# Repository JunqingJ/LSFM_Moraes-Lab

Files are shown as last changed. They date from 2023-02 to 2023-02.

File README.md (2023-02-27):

# LSFM_Moraes-Lab
A customized Oblique Plane Microscope (OPM) based on the design of SCPAE 2.0 published by Prof. Hillman. The microscope is primarily customized to image non-cleared brain organoids during the early development stage for quality control purposes.

The repository is currently work in progress and will eventually contain all information (alignment procedure, part list, design files for machined items, controlling code) need to re-build the same setup.

It is also highly suggested for anyone new to light-sheet microscopy to consult Alfred Millett-Sikking's work(https://github.com/amsikking). The setup shown in this repository had received tremendous amount of help form Alfred and many design is also inspired by his work. 

Schematic diagram of the setup:

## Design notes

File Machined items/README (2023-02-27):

ARCOpticThreads.xml - Threading file for Fusion 360 to generate internal/external SM1 threading. 
To use it, add the .xml file into local threading data folder of Fusion360
Folder address ((C:\Users\%Username%\AppData\Local\Autodesk\webdeploy\production\%Version number%\Fusion\Server\Fusion\Configuration\ThreadData))

CCM_G01 side mount plate - Fusion 360 design file. CCM_G01 is design to turn the light in xy plane. In case the light to be turned into z axis, a side mounting is need

Sample stage arm - the stage arm is designed to fit onto Picard 4D stage to hold a 35mm petri dish with set screw

Slide git Powell mount - The mount is designed to adapt a 8.9mm Powell lens from Laserline Optics into 30mm cage palte from Thorlabs. 
It is important to ask for Slide fit when machining

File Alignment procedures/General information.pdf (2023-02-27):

General information

The overall setup of the microscope is shown in Figure 1 with laser been represented by blue and

fluorescent light been represented by green. The overall setup is further divided into 4 subsections

for details of alignment procedures and equipment used for assembling will be listed at the end of

each section. It should be noticed that all optics were setup on a secondary breadboard that was

elevated around 5inch higher than the optical table. The illumination laser was setup on a separate

breadboard that is elevated around 1.5inch higher than the first one. This is done so that it provides

enough space in z-direction for the alignment of optics and electronics could also been housed

under elevated breadboard to save space. In addition, a bright-field imaging system was added in

section 1 by using a removable turning mirror 2, S3, T4 and camera 2. This is done so that it

provides the system a much easier way to locate the sample and the region of interest prior to the

3D scanning.

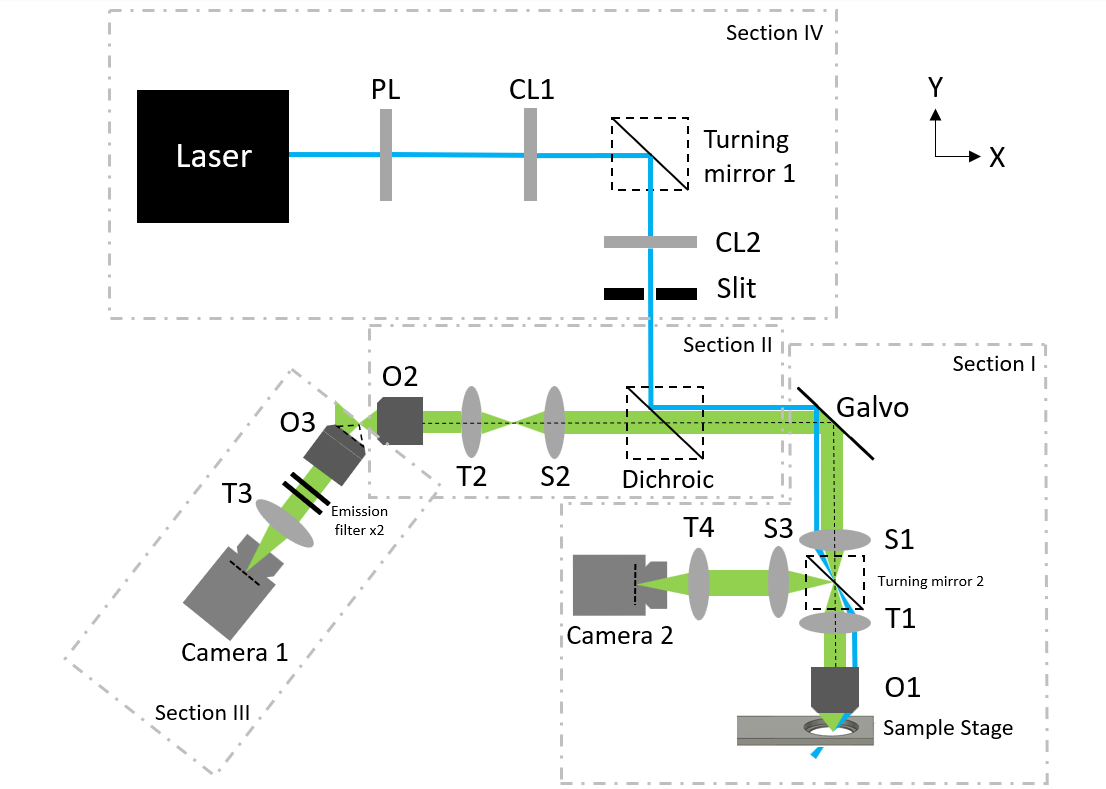
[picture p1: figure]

Figure 1 Overall setup of the microscope with subsections

Apart from the equipment and tools used in individual sections, several other equipment was used

throughout the entire process for the calibration and mounting purpose. Cage system is widely

used within the system to facilitate easier mounting and alignment. Both 30mm and 60mm cage

system are used due to the need of lens in different size. As a result, generic naming will be used

regarding cage system in subsections and the amount used will be detailed in tables. For calibration

purpose, a shear plate compatible with beam size from 1-3mm (Thorlabs, SI035) were used to test

collimation of beams. Another 4.5mW collimated laser module at 532nm with 3.5mm round beam

size (Thorlabs, CPS532) were used to assist the alignment. The collimated laser module was fitted

into the 30mm cage system by a SM1-threaded adaptor (Thorlabs, AD11F) and mounted onto a

quick-release cage plate (Thorlabs, CP44F). In addition, both post-mountable and cage system iris

diaphragms (Thorlabs, ID25 and CP20D) were used for lens positioning. Finally, laser viewing

cards (Thorlabs, VRC1 and VRC2) were used to visualize the laser beam while minimizing its

potential harm to eyes.

Before any part of the microscope was assembled, a 30×48inch optical table with 4inch thick

breadboard (Newport, VIS3048-PG4-325A) was inflated using compressed nitrogen. The flatness

of the surface was first checked by making sure the bubble leveler on each stand of the optical

table was centered. After that, illumination laser (HUBNER Photonics) was used, and the height

of the laser beam was measured over a long distance for verification. It is important to use the

minimal laser power available (~1mW) during the flatness verification and a laser safety glass (ex.

Thorlabs, LG14) should be used based on the wavelength of the laser used.

Table 1 General items used throughout all alignment processes

Item description | Part number (Vendor)
Shear plate (1-3mm beam diameter) | SI035(Thorlabs)
Collimated laser module, 532nm | CPS532(Thorlabs)
SM1-threaded adaptor | AD11F(Thorlabs)
Quick-release cage plate | CP44F(Thorlabs)
Post-mountable Iris diaphragms | ID25(Thorlabs)
30mm cage system Iris diaphragms | CP20D(Thorlabs)

Laser viewing cards (UV/Vis and Vis/NIR) | VRC1, VRC2(Thorlabs)
Laser safety glass | LG14(Thorlabs)
Illumination laser, 488nm | C-flex Series(HUBNER Photonics)
30×48inch optical table | VIS3048-PG4-325A(Newport)

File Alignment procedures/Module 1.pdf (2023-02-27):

Module 1

The general layout and real setup of module 1 is shown in Figure 1 and it serves for 4 functions

within the microscope: light-sheet scanning, fluorescent de-scanning, aligning laser enlargement

and bright-field imaging. An aligning laser enlargement module is used so that its small laser spot

could eventually overfill the back aperture of O2 in module 2 for easier alignment. Regular setup

where aligning laser replaces O1 during the alignment would results in 0.83X demagnification of

laser spot, compared with 4.16X magnification with enlargement module used.

For a perfect parallel light-sheet translation on the sample, the image point on galvo needs to be

relayed on to the back focal plane within O1. Thus, a 4-f system needs to be formed between galvo

mirror and O1. In addition, a well-aligned 4-f system also ensures proper de-scanning of the image.

Otherwise, a linear translation of images will be observed on the camera. Finally, it should be

noted that the collimation and divergence of the light-sheet would be different depends on angle

of viewing as illustrated in Figure 2.

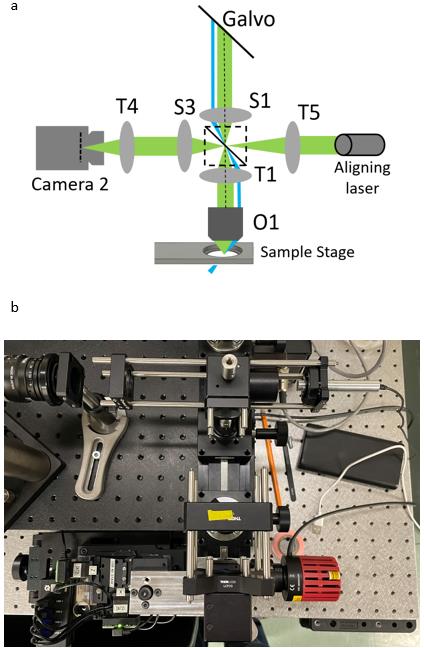
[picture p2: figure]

Figure 1 a) Schematic layout of module 1; b) Real setup of module 1

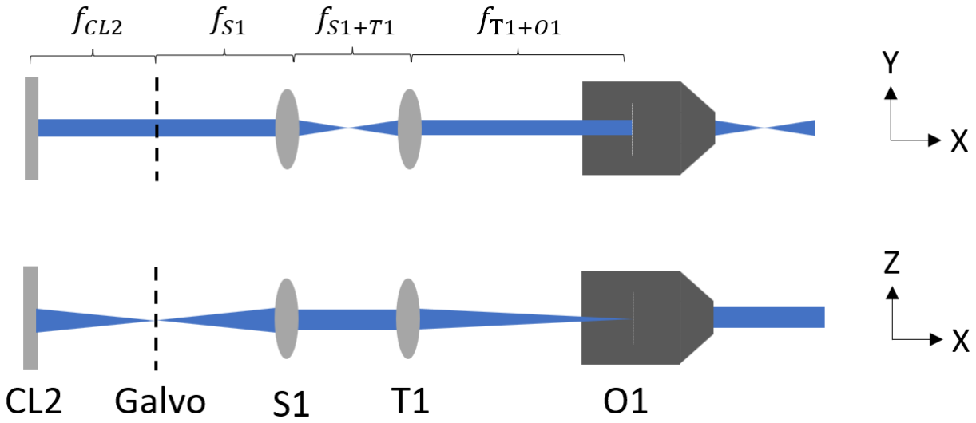
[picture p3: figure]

Figure 2 Collimation and divergence of light-sheet viewing from different axis

For major components used for light-sheet microscope, one 12inch travel rack and 3 pinion stages

(Edmund Optics, 59-334 and 59-331) are required and a 1D large beam galvo-mirror (Thorlabs,

GVS011) is needed to avoid image clipping. Both S1 and T1 are mounted using 60mm cage plate,

½’’ post and post holder. The high numerical aperture water immersion objective O1 (Olympus,

XLUMPLFLN20XW) was connected with T1 through a 30mm-60mm cage adaptor (Thorlabs,

LCP33). After that, a 30mm cage compatible turning cube (Thorlabs, CCM-G01) was used to turn

the scanning light-sheet downwards for easier water immersion during the imaging process.

For major components used for bright-field imaging, a rectangular mirror (Thorlabs, FM03R) is

housed using a 30mm cage cube (Thorlabs, CM1-DCH). The cage cube was mounted upside down

so that its base where the mirror is attached could be removed freely to enable or disable the

function of bright-field imaging. A 75mm achromatic doublets (Thorlabs, AC254-075-A) was

mounted using lens tube as S3 and a 35mm machine vision camera lens (Thorlabs, MVL35M1)

was used as T4. As the bright-field imaging only serves for easier sample location, a light weight,

compact scientific camera (Thorlabs, CS165MU) was used. In addition, two more mounting

adaptors (Thorlabs, SM1A57; Edmund Optics, 12484) were used to fit the camera into a 30mm

cage plate. Finally, a mounted LED (Thorlabs, M450LP2) attached with collimator (Thorlabs,

SM1U25A) was used as the light source for bright-field microscope.

For the setup of elevated breadboard, 2 separate board with size 12×18inch and 24×24inch

(Thorlabs, MB1218 and MB2424) were used for illumination module and the rest of microscope

system. One tapped hole at each corner of the breadboard was machined into a clearance hole so

it can be aligned with the optical table using 1.5’’ posts.

Setting up reference points:

1. Mount both galvo mirror and S1 using ½’’ post and post mount, both their x-y location and

height does not need to be precise

2. Turn on illumination laser and set it to the minimal power
3. Bring the galvo mirror in front of the laser. Adjust the height of ½’’ post to make sure laser

centers on galvo mirror’s z-axis. Depends on the manufacturer of the galvo mirror, its

rotation center may not be the same as its mounting center. A customized plate may be

required to fix it.

4. Tighten the set screw and use a post collar on galvo mirror’s post to mark and fix its height
5. Mount the post holder of S1 onto the front most manual stage on the translation rack
6. Use 2 sets of cage rod and a 30-60mm cage adaptor to connect an iris to the back of S1
7. Bring the entire rack with S1 attached in front of the laser. Adjust both position of the rack

and height of ½’’ post to make sure laser passing through the iris hole after S1

8. Tighten the set screw and use a post collar on S1’s post to mark and fix its height. This will

be the primary height reference for the rest of microscope system

Setting up O1 objective:

1. Use a C-SM1 mounting adaptor to connect O1 objective onto a 30mm cage plate
2. Use 1 set of cage rod to connect the cage plate onto a cubic turning mirror, add another set

of cage rod on the other side of the cubic turning mirror for future mounting. Making sure

the additional set of cage rod used are short enough

3. Mount T1 using a 60mm cage plate and use 1 set of cage rod to connect it with a 30-60mm

cage adaptor

4. Remove screws from 1 set of cage rod and slide them into aligning laser’s cage plate
5. Connect screwless cage rod with the rod used in step 2 so that aligning laser and front-end

of the objective are face-to-face

6. Slide the additional set of cage rod from step 2 into the cage adaptor. Making sure it slides

all the way to the end before tightening (figure)

7. Put on laser safety glass and turn on aligning laser, a spherical laser spot should be observed

behind the T1

8. Slightly loosen the set screw on the outer holes of 30-60mm cage adaptor to slide the cage

adaptor back and forth

9. Place the shear plate in the center of the laser spot. Keep adjusting the position of the cage

adaptor until the shearing pattern is parallel to the reference line

10. Tighten the set screw on cage adaptor and remove the aligning laser by unscrewing the rod

connected in step 5. The relayed system between T1 and O1 is now formed

Setting up 4f system:

1. Mount the translation rack on the right side of the breadboard, making sure its back end

(oppose to the side with S1 mounted) is aligned with the edge of breadboard

2. Insert aligning laser in in cage adaptor connected to S1.
3. Place 2 post mountable iris in front of S1, making sure they are not too close with each

other. Use the aligning laser coming out of S1 to adjust the height of iris

4. Once the height of irises are fixed, loosen the set screw on S1 and rotate it until the aligning

laser passing through the center of both iris

5. Remove aligning laser from S1 and use it to replace the cubic turning mirror that slides

into T1’s cage adaptor

6. Mount T1 on the back most stage on the translation rack, leaving the middle one for bright-

field imaging system

7. Turn on the aligning laser and adjust both the height and rotation of T1 until the light

coming after S1 passing through the center of both iris.

8. Tighten the set screw and use a post collar to fix the height of T1
9. Remove irises and move the aligning laser back to the cage adaptor on S1
10. Mount galvo mirror at top right corner of the breadboard. Making sure to use the closest

hole available in front of the S1. By using tapped holes available on breadboard, the center

of galvo mirror and S1 should be auto-aligned

11. Using the knob on the translation stage to adjust the position of S1 until the laser spot is

focused on the galvo mirror. Use the set screw on the stage to fix its position

12. Move the aligning laser to the cage adaptor on T1 and adjust its position using the knob
13. Place the shear plate in the center of laser reflected by galvo mirror and adjust the position

of T1 until the shear pattern is parallel to the reference line

14. Remove the aligning laser and put back the cubic turning mirror attached with O1 objective.

The 4f system in module 1 is setup

Setting up bright-field imaging system and laser enlargement:

1. Ensure all above alignment procedures are complete and place the aligning laser on T1 by

switching off O1 objectives

2. Place 2 post mount iris after galvo mirror, adjust their height to the same level of reflected

beam from galvo mirror

3. Use Matlab to control the angle of galvo mirror (details can be found in control section)

until the laser beam passes the center of both iris

4. Thread T4 onto the camera and then use both M35.5-T mount adaptor and T-SM1 mount

adaptor to mount front-end of T4 onto a 30mm cage plate

5. Use 2 separate lens tube to mount both S3 and T5. Then mount S3 onto a 30mm cage plate

and T5 directly onto the cage cube. 2 different side of the cage cube that are opposite to

each other should be used

6. Remove aligning laser from T1, then use 2 sets of cage rods to mount camera, S3 and

aligning laser onto the cage tube. The positioning does not need to be precise

7. Mount the cage cube (with mirror attached to the base) upside down onto the middle stage

on the track and turn on the aligning laser

8. Adjust the rotation and height of the cage cube mount until the laser passes the center of

both iris setup in step 2

9. Tighten the mount of cage cube and adjust the location of the manual stage using the knob

until the laser reflected from galvo is collimated (use shear plate for confirmation)

10. Switch the aligning laser back onto T1 and adjust the position of S3 until the light coming

out from it is collimated

11. Put the aligning laser back onto the cage cube and place back the O1 objective. Both bright-

field imaging system and laser enlargement is now set up. The bright-field imaging system

can be turned on or off by simply keep or remove the mirror in the cage cube

Table 1 Part list for module 1

Optical Part | Part description | Part number (Vendor)
Galvo mirror | 1D large beam scanner | GVS011 (Thorlabs)
S1 | 75mm achromat | 49-292 (Edmund Optics)
T1 | 150mm achromat | 49-285 (Edmund Optics)
O1 | XLUMPLFLN 20x/1.0NA W | XLUMPLFLN20XW
| | (Olympus)
T5 | 30mm mounted achromatic doublet | AC254-030-A-ML
| | (Thorlabs)
S3 | 75mm achromatic doublet | AC254-075-A (Thorlabs)
T4 | 35 mm EFL, f/1.4 | MVL35M1 (Thorlabs)
Removable mirror | 25×36mm visible cold mirror | FM03R (Thorlabs)
Bright-field camera | 1.6MP monochrome CMOS camera | CS165MU (Thorlabs)
Mounting part | Part description | Part number (Vendor)
Cage Cube | 30mm cage cube for rectangular Optics | CM1-DCH (Thorlabs)
Travel track | 12'' pinion track | 59-334 (Edmund Optics)
Manual track stage ×3 | 1 Knob stage | 59-331 (Edmund Optics)
60mm cage plate ×2 | SM2 threaded, 0.9'' thick | LCP34T (Thorlabs)
30-60mm cage adaptor ×2 | 0.5'' thick | LCP33 (Thorlabs)
Turning mirror | 30mm cage turning mirror | CCMG01 (Thorlabs)
Lens tube ×2 | 1'' lens tube, SM1 threaded | SM1L10 (Thorlabs)
30mm cage plate ×2 | 0.35'' thick, SM1 threaded | CP33 (Thorlabs)
M35.5 to T mount adaptor | M35.5 external and T mount internal | 12484 (Edmund Optics)
T mount to SM1 adaptor | T mount external and SM1 internal | SM1A57 (Thorlabs)
1.5'' post ×2 | 1/2'' optical post | TR1.5 (Thorlabs)
0.75'' post ×2 | 1/2'' optical post | TR075 (Thorlabs)
Cage rod set ×5 | Length varied depends actual need | (Thorlabs)
1'' post holder ×2 | 1/2'' post holder | PH1 (Thorlabs)

1.5'' post holder ×2 | 1/2'' post holder | PH1.5 (Thorlabs)
Post collar ×3 | Thin slip-on post collar | R2T (Thorlabs)

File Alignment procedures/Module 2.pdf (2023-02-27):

Module 2

The general layout of module 2 is shown in Figure 1 and it mainly serves for image relay and

magnification adjustment. As Sine and Hershel condition requires a magnification of 1.33 between

the focal point of O1 and O2, an extra pair of relay lens is need for such magnification adjustment

purpose. The major alignment goal for module 2 is to form a 4-f system which follows similar

procedures as mentioned in module 1.

Figure 1 General layout of Module 2

For major components used for module 2, one 12’’ travel track with 3 one-knob stages from

Edmund Optics were used. A 30mm cage cube for rectangular optics from Thorlabs was used to

house dichroic mirrors (Thorlabs, DMLP505R and DMLP605R) that matches the excitation and

emission spectrum of the laser. A pair of 60mm and 100mm achromatic lens (Thorlabs, AC254-

060-A and Edmund Optics, 49-284-INK) were used as S2 and T2. Finally, a 20X, high NA air

objective (Nikon, CFI Plan Apo Lambda 20x/0.75 NA) were used as O2.

Alignment for module 2:

1. Mount the long travel rack onto the breadboard, the center of optics mount should be auto

aligned with the center of galvo by doing so

2. Place 2 post mountable iris on the second and third one-knob stage and use them to confirm

module 1 is well aligned. The laser spot reflected from galvo mirror should be travelling

path is perfectly aligned with the breadboard in all xyz axis. The collimation of the laser

should be checked using shear plate. Do not remove iris after this step

3. Using a lens tube to mount S2 before threading it onto the dichroic cage cube

4. Threading a set of cage rod to dichroic cage cube on the side with S2 mounted. Then mount

a 30mm cage cube onto the cage rod relatively close to S2. The position doesn’t need to be

precise. This will be referred as “S2-dichroic” in later steps

5. Unthread T5 in module 1, the laser beam should now focused onto the galvo mirror. After

that, mount S2-dichroic using post on the first one-knob stage.

6. Adjust the height and rotation of S2-dichroic until the laser beam passes through the center

of both iris

7. Using shear plate to check if the laser beam after S2-dichroic is collimated. Adjust the

position of one-knob stage on the track until the laser is collimated. It should be noticed

that the space between S2-dichroic is very limited, adjust the spacing between the 30mm

cage plate and S2 in step 4 if needed

8. Remove the iris from the second stage and placed somewhere further along breadboard’s

tapped hole for later reference. Thread T5 back in module 1 and mount T2 using a 60mm

cage plate

9. Mount T2 on the second one-knob stage. Adjust its height and rotation until the laser beam

passes both iris. Using shear plate as reference and adjust the position of the stage until

laser coming out of T2 is collimated

10. Remove both iris and aligning laser in module 1. Mount a cage compatible iris onto the

position where aligning laser used to be.

11. Using a C-SM1 adaptor to thread O2 onto a 30mm cage plate. Using a set of cage rod to

mount the aligning laser directly on the front side of the O2

12. Mount O2 onto the third one-knob stage using post. Then turn on the laser and adjust both

height and rotation of O2 until the laser beam passes the center of iris in step 10

13. Unthread T5 and use the shear plate to check laser’s collimation. Adjust the stage with O2

mounted until the laser coming after the iris is collimated

14. Remove the aligning laser from O2’s mounting plate. Remove the iris from step 10 and

place back the aligning laser. Do not thread back T5

15. Mount the iris on the back side of O2’s plate. Turn on aligning laser and readjust the height

and rotation of O2 until the laser beam coming through T2 passing the center of iris

16. Remove iris from O2 and thread back T5. Module 2 is now fully aligned as a 4f system.

The dichroic mirror can either be removed or inserted during the alignment as it does not

affect the pathway of laser

Table 1 Part list for module 2

Optical Part | Part description | Part number (Vendor)
Dichroic mirror for GFP | 505nm cut-on long-pass dichroic mirror | DMLP505R (Thorlabs)
Dichroic mirror for Tritc | 605nm cut-on long-pass dichroic mirror | DMLP605R (Thorlabs)
S2 | 60mm achromat | AC254-060-A (Thorlabs)
T2 | 100mm achromat | 49-284 (Edmund Optics)
O2 | CFI Plan Apo Lambda 20x/0.75 NA | (Nikon)
Mounting part | Part description | Part number (Vendor)
Cage Cube | 30mm cage cube for rectangular Optics | CM1-DCH (Thorlabs)
Travel track | 12'' pinion track | 59-334 (Edmund Optics)
Manual track stage ×3 | 1 Knob stage | 59-331 (Edmund Optics)
60mm cage plate | SM2 threaded, 0.9'' thick | LCP34T (Thorlabs)
Lens tube | 1'' lens tube, SM1 threaded | SM1L10 (Thorlabs)
30mm cage plate ×2 | 0.35'' thick, SM1 threaded | CP33 (Thorlabs)
C mount to SM1 adaptor | C mount internal to SM1 external | SM1A10 (Thorlabs)
1.5'' post ×2 | 1/2'' optical post | TR1.5 (Thorlabs)
0.75'' post | 1/2'' optical post | TR075 (Thorlabs)
Cage rod set ×2 | Length varied depends on actual need | (Thorlabs)
1'' post holder | 1/2'' post holder | PH1 (Thorlabs)
1.5'' post holder ×2 | 1/2'' post holder | PH1.5 (Thorlabs)
Post collar ×3 | Thin slip-on post collar | R2T (Thorlabs)

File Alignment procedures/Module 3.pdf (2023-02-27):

Module 3

The general layout of module 3 is shown in Figure 1 and it mainly serves to reimage the aberration

corrected but still tilted image onto the camera. It should be noticed that a right-angle turning

mirror can be placed behind O3 if the length of optical table was not sufficient for the linear layout

of module 3. In addition, 2 identical emission filters were used in series as the reflection of light-

sheet could not be fully blocked with the use of one single filter. The choice of O3 dictates the

overall magnification range of the system. A commercial photography zoom lens was chosen over

microscopy camera lens with fixed focal distance so that it gives some flexibility in adjustment of

magnification. Furthermore, both T3 and camera were mounted vertically for easier aligning. As

a result, another right-angle turning mirror was used after emission filters to direct the light upward.

Finally, the assembly and alignment of module 3 is rather simply compared to other modules as it

does not require a 4f system setup. However, the alignment between module 2 and module 3 is the

most important and hardest part of the entire system. Detailed step by step procedure will be

presented in Error! Reference source not found..

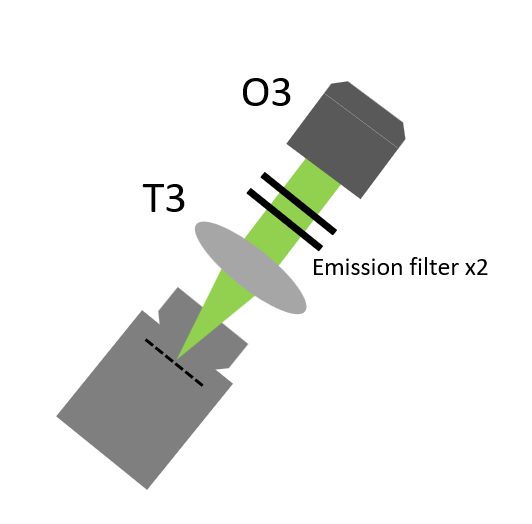
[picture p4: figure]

Figure 1 General layout of module 3

For major optical components used in module 3, a 20X, high NA dry objective (Edmund Optics,

58-373) was used. However, the choice of O3 is rather flexible and another 10X, high NA dry objective (Nikon, CFI Plan Apo Lambda 10x/0.45 NA) can also be used as alternative. 2 sets of

pre-mounted emission filters for GFP and Tritc (Thorlabs, MF525-39 and MF620-52) were used

with 2 manual filter wheels (Thorlabs, CFW6). A commercial photography zoom lens (Canon, EF

70-200 f/2.8L IS III) was used as T3 for flexible magnification adjustment. Finally, a sCMOS

camera (Andor Oxford instrument, Zyla 4.2+) was used to capture final images.

Alignment for module 3:

1. Using a C-SM1 adaptor to mount O3 onto a right-angle turning mirror cube. Then use a

post, post holder, base adaptor and clamping fork to secure O3 onto a 4’’×6’’ breadboard

2. Using a set of cage rod to mount a cage compatible iris on the exiting side of the turning

mirror cube

3. Turn on the aligning laser and place O3 head to head toward O2. The angle between O2

and O3 should be roughly 180° and the spacing should roughly be 15mm (WDO2 + WDO3)

4. Adjust the height of O3 until the light from the backside of O3 passes through the center

of iris. Tightly secure the side screw of post holder and use a post collar to further fix its

height

5. Remove iris and mount 2 manual filter wheel in series on the exit side of the turning cube.

It should be noticed that only bottom 2 cage rodsshould be used according to the instruction

of the filter wheel

6. Slide in another 30mm cage plate with post after emission filters. Then mount a turning

mirror onto the cage plate with top 2 cage rod threaded only

7. Machine the long travel vertical stage that it is securely connected to the tripod mount for

T3

8. Thread an EOS-C mount adaptor onto T3 and carefully insert it into the vertically mounted

tripod before connect it to the camera. Firmly secure the tripod

9. All components in module 3 is now set up. All components before T3 were mounted on

one single breadboard and will be referred as “the breadboard plate” in section Error!

Reference source not found.

Table 1 Part list for module 3

Optical Part | Part description | Part number (Vendor)

O3 | EO HR 20x/0.60 NA | 58-373 (Edmund Optics)
GFP emission filter ×2 | CW=525, BW=39 | MF525-39 (Thorlabs)
Tritc emission filter ×2 | CW=620, BW=52 | MF620-52 (Thorlabs)
T3 | 70-200mm, f/2.8 Zoom | EF 70-200 f/2.8L IS III (Canon)
Camera | sCMOS | Zyla 4.2+ (Andor Oxford Instruments)
Mounting | Part description | Part number (Vendor)
Breadboard | 4''x6'', tapped | MB4 (Thorlabs)
C mount to SM1 adaptor | C mount internal to SM1 external | SM1A10 (Thorlabs)
Turning mirror ×2 | 30mm cage turning mirror | CCMG01 (Thorlabs)
filter wheel ×2 | 30mm cage manual filter wheel | CFW6
EOS-C mount adaptor | C mount external, EOS internal | (Amazon)
Tripod | tripod for Canon 70-200 lens | (Amazon)
vertical translation stage | 10'' vertical travel | VAP10 (Thorlabs)
30mm cage plate | 0.35'' thick, SM1 threaded | CP33 (Thorlabs)
Cage rod set | Length varied depends on need | (Thorlabs)
1.5'' post ×2 | 1/2'' optical post | TR1.5 (Thorlabs)
1.5'' post holder ×2 | 1/2'' post holder | PH1.5 (Thorlabs)
Base adaptor ×2 | 1.25'' pedestal base adaptor | BE1 (Thorlabs)
Table clamp ×2 | 1/4'' 20 tapped | CL2 (Thorlabs)

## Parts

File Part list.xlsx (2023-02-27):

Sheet: General
Item description | Part number (Vendor)
Shear plate (1-3mm beam diameter) | SI035(Thorlabs)
Collimated laser module, 532nm | CPS532(Thorlabs)
SM1-threaded adaptor | AD11F(Thorlabs)
Quick-release cage plate | CP44F(Thorlabs)
Post-mountable Iris diaphragms | ID25(Thorlabs)
30mm cage system Iris diaphragms | CP20D(Thorlabs)
Laser viewing cards (UV/Vis and Vis/NIR) | VRC1, VRC2(Thorlabs)
Laser safety glass | LG14(Thorlabs)
Illumination laser, 488nm | C-flex Series(HUBNER Photonics)
30''x48'' optical table | VIS3048-PG4-325A(Newport)

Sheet: Module 1
Optical Part | Part description | Part number (Vendor)
Galvo mirror | 1D large beam scanner | GVS011 (Thorlabs)
S1 | 75mm achromat | 49-292 (Edmund Optics)
T1 | 150mm achromat | 49-285 (Edmund Optics)
O1 | XLUMPLFLN 20x/1.0NA W | XLUMPLFLN20XW (Olympus)
T5 | 30mm mounted achromatic doublet | AC254-030-A-ML (Thorlabs)
S3 | 75mm achromatic doublet | AC254-075-A (Thorlabs)
T4 | 35 mm EFL, f/1.4 | MVL35M1 (Thorlabs)
Removable mirror | 25x36mm visible cold mirror | FM03R (Thorlabs)
Bright-field camera | 1.6MP monochrome CMOS camera | CS165MU (Thorlabs)
Mounting | Part description | Part number (Vendor)
Cage Cube | 30mm cage cube for rectangular Optics | CM1-DCH (Thorlabs)
Travel track | 12'' pinion track | 59-334 (Edmund Optics)
Manual track stage x3 | 1 Knob stage | 59-331 (Edmund Optics)
60mm cage plate x2 | SM2 threaded, 0.9'' thick | LCP34T (Thorlabs)
30-60mm cage adaptor x2 | 0.5'' thick | LCP33 (Thorlabs)
Turning mirror | 30mm cage turning mirror | CCMG01 (Thorlabs)
Lens tube x2 | 1'' lens tube, SM1 threaded | SM1L10 (Thorlabs)
30mm cage plate x2 | 0.35'' thick, SM1 threaded | CP33 (Thorlabs)
M35.5 to T mount adaptor | M35.5 external and T mount internal | 12484 (Edmund Optics)
T mount to SM1 adaptor | T mount external and SM1 internal | SM1A57 (Thorlabs)
1.5'' post x2 | 1/2'' optical post | TR1.5 (Thorlabs)
0.75'' post x2 | 1/2'' optical post | TR075 (Thorlabs)
Cage rod set x5 | Length varied depends on actual need | (Thorlabs)
1'' post holder x2 | 1/2'' post holder | PH1 (Thorlabs)
1.5'' post holder x2 | 1/2'' post holder | PH1.5 (Thorlabs)
Post collar x3 | thin slip-on post holder | R2T (Thorlabs)

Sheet: Module 2
Optical Part | Part description | Part number (Vendor)
Dichroic mirror for GFP | 505nm cut-on longpass dichroic mirror | DMLP505R (Thorlabs)
Dichroic mirror for Tritc | 605nm cut-on longpass dichroic mirror | DMLP605R (Thorlabs)
S2 | 60mm achromat | AC254-060-A (Thorlabs)
T2 | 100mm achromat | 49-284-INK (Edmund Optics)
O2 | CFI Plan Apo Lambda 20x/0.75 NA | (Nikon)
Mounting | Part description | Part number (Vendor)
Cage Cube | 30mm cage cube for rectangular Optics | CM1-DCH (Thorlabs)
Travel track | 12'' pinion track | 59-334 (Edmund Optics)
Manual track stage x3 | 1 Knob stage | 59-331 (Edmund Optics)
60mm cage plate | SM2 threaded, 0.9'' thick | LCP34T (Thorlabs)
Lens tube | 1'' lens tube, SM1 threaded | SM1L10 (Thorlabs)
30mm cage plate x2 | 0.35'' thick, SM1 threaded | CP33 (Thorlabs)
C mount to SM1 adaptor | C mount internal to SM1 external | SM1A10 (Thorlabs)
1.5'' post x2 | 1/2'' optical post | TR1.5 (Thorlabs)
0.75'' post | 1/2'' optical post | TR075 (Thorlabs)
Cage rod set x2 | Length varied depends on actual need | (Thorlabs)
1'' post holder | 1/2'' post holder | PH1 (Thorlabs)
1.5'' post holder x2 | 1/2'' post holder | PH1.5 (Thorlabs)
Post collar x3 | thin slip-on post holder | R2T (Thorlabs)

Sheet: Module 3
Optical Part | Part description | Part number (Vendor)
O3 | EO HR 20x/0.60 NA | 58-373 (Edmund Optics)
GFP emission filter x2 | CW=525, BW=39 | MF525-39 (Thorlabs)
Tritc emission filter x2 | CW=620, BW=52 | MF620-52 (Thorlabs)
T3 | 70-200mm, f/2.8 Zoom | EF 70-200 f/2.8L IS III (Canon)
Camera | sCMOS | Zyla 4.2+ (Andor Oxford Instruments)
Mounting | Part description | Part number (Vendor)
Breadboard | 4''x6'', tapped | MB4 (Thorlabs)
C mount to SM1 adaptor | C mount internal to SM1 external | SM1A10 (Thorlabs)
Turning mirror x2 | 30mm cage turning mirror | CCMG01 (Thorlabs)
filter wheel x2 | 30mm cage manual filter wheel | CFW6
EOS-C mount adaptor | C mount external and EOS internal | (Amazon)
Tripod | tripod for Canon EF 70-200 f/2.8L IS III | (Amazon)
vertical translation stage | 10'' vertical travel | VAP10 (Thorlabs)
30mm cage plate | 0.35'' thick, SM1 threaded | CP33 (Thorlabs)
Cage rod set | Length varied depends on actual need | (Thorlabs)
1.5'' post x2 | 1/2'' optical post | TR1.5 (Thorlabs)
1.5'' post holder x2 | 1/2'' post holder | PH1.5 (Thorlabs)
Base adaptor x2 | 1.25'' pedestal base adaptor | BE1 (Thorlabs)
Table clamp x2 | 1/4'' 20 tapped | CL2 (Thorlabs)

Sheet: Module 4
Optical Part | Part description | Part number (Vendor)

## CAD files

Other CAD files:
Machined items/CCM_G01 side mounting plate.f3d
Machined items/GVS011 mounting plate.f3d
Machined items/sample stage arm.f3d
Machined items/slide fit Powell mount.f3d

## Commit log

2021-12-20 Create Customized mounting
2021-12-20 Update Customized mounting
2021-12-20 Create Powell lens
2021-12-20 Add files via upload
    Powell lens from Laserline Optics (LOCP-8.9R30-0.8)
    The mounting piece adapts the cylindrical lens to standard Thorlabs 16mm cage system with SM1 thread
    [Powell mount.stl]
2021-12-20 Add files via upload
    Powell lens available from Laserline Optics (LOCP-8.9R30-0.8)
    The mounting pieces adapts the cylindrical lens to standard Thorlabs 16mm cage system with SM1 thread
    [Powell mount.stl]
2022-03-03 Add files via upload
    Thorlabs standard internal and external SM1 threading for Fusion 360. Credit: anoymous online user
